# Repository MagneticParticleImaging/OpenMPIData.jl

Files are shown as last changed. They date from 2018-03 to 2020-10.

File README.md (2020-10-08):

# OpenMPIData



The aim of this project is to provide MPI data that are openly available for the research
community and can be freely used. You can find detailed description on the project under
the following link:



## How to give credit
If you use this package please acknowledge us by citing:

T. Knopp, P. Szwargulski, F. Griese, M. Gräser (2020). OpenMPIData: An initiative for freely accessible magnetic particle imaging data. *Data in Brief.* **28** 104971.

A BibTeX file is directly contained within this package `OpenMPIData.bib`.

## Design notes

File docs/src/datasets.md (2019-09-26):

# Datasets

The phantoms have been acquired with specific measurement sequences, MPI scanners, and tracer material.
In the following table an overview about all datasets is given:

## Phantom Measurements

| Study | Experiment Number | Scanner | Sequence | Tracer |
|---|---|---|---|---|
| shapePhantom | 1 | Bruker | 1D Cartesian | Perimag |
| shapePhantom | 2 | Bruker | 2D Lissajous | Perimag |
| shapePhantom | 3 | Bruker | 3D Lissajous | Perimag |
| resolutionPhantom | 1 | Bruker | 1D Cartesian | Perimag |
| resolutionPhantom | 2 | Bruker | 2D Lissajous | Perimag |
| resolutionPhantom | 3 | Bruker | 3D Lissajous | Perimag |
| concentrationPhantom | 1 | Bruker | 1D Cartesian | Perimag |
| concentrationPhantom | 2 | Bruker | 2D Lissajous | Perimag |
| concentrationPhantom | 3 | Bruker | 3D Lissajous | Perimag |
| rotationPhantom | 1 | Bruker | 3D Lissajous | Perimag |
| rotationPhantom | 2 | Bruker | 3D Lissajous | Perimag |
| rotationPhantom | 3 | Bruker | 3D Lissajous | Perimag |

In addition several calibration measurements are available:

## Calibration Measurements

| Study | Experiment Number | Scanner | Sequence | Tracer | Grid | FoV |
|---|---|---|---|---|---|---|
| calibration | 1 | Bruker | 1D Cartesian | Perimag |19x19x19|38x38x19|
| calibration | 2 | Bruker | 2D Lissajous | Perimag |19x19x19|38x38x19|
| calibration | 3 | Bruker | 3D Lissajous | Perimag |19x19x19|38x38x19|
| calibration | 4 | Bruker | 1D Cartesian | Perimag |37x37x37|37x37x18.5|
| calibration | 5 | Bruker | 2D Lissajous | Perimag |37x37x37|37x37x18.5|
| calibration | 6 | Bruker | 3D Lissajous | Perimag |37x37x37|37x37x18.5|
| calibration | 7 | Bruker | 3D Lissajous | Synomag-D |37x37x37|37x37x18.5|
| calibration | 8 | Bruker | 3D Lissajous | Perimag |33x33x27|66x66x27|
| calibration | 9 | Bruker | 3D Lissajous | Perimag |33x33x27|66x66x27|
| calibration | 10 | Bruker | 3D Lissajous | Perimag |33x33x27|66x66x27|
| calibration | 11 | Bruker | 3D Lissajous | Perimag |33x33x27|66x66x27|
| calibration | 12 | Bruker | 3D Lissajous | Perimag |33x33x27|66x66x27|
| calibration | 13 | Bruker | 3D Lissajous | Perimag |33x33x27|66x66x27|
| calibration | 14 | Bruker | 3D Lissajous | Perimag |33x33x27|66x66x27|
| calibration | 15 | Bruker | 3D Lissajous | Perimag |33x33x27|66x66x27|

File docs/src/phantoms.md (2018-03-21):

# Phantoms

Here, we describe the phantoms being used during the MPI measurements. The phantoms are all printed with the stereolithography 3D printing technique. All phantoms share the same robot mount defining the coordinate system. The robot mount is fixed in positive X direction. The flat side marks the positive Z direction. Poistive Y direction is then defined by right hand rule.

You can download the phantoms construction files in the format .SLDPRT, .STL and .STEP.

## Shape Phantom

To resemble a well known shape a cone defined by a **1 mm** radius tip and an apex angle of **10 deg** and a hight of **22 mm**. The total volume is **683.9 µL**. As tracer **Perimag** in a concentration of **50 mmol/L** were used. The phantom can be rendered in 3D resemling the cone or can be cut in a layer view to see either a circle (YZ plane) or a triangle with flattened tip (XZ or XY plane)

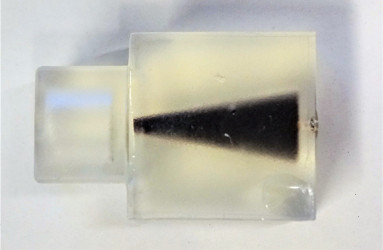
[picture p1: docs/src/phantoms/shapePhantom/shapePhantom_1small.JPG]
ShapePhantom


### CAD Data Shape Phantom

[SolidWorks Part File](./phantoms/shapePhantom/Phantom3_Shape.SLDPRT)
[STL File](./phantoms/shapePhantom/Phantom3_Shape.STL)
[STEP File](./phantoms/shapePhantom/Phantom3_Shape.STEP)

## Resolution Phantom

The resolution phantom consits of 5 tubes filled with **Perimag** featuring a concentration of **50 mmol**.
The 5 tubes have a common origin on one side of the phantom. From there the extend in different angles from this origin within the XY and the YZ plane. As the imaging system features the strong gradient in Z direction the angles in the YZ plane are chosen smaller (**10 deg and 15 deg**) than in XY direction (**20 deg and 30 deg**).
By chosing different planes, one can determine the capable resolution due to different distances of the tubes.

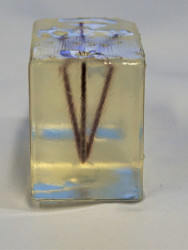
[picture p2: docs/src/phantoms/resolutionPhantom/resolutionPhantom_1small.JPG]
Resolution Phantom


### CAD Data Resolution Phantom

[SolidWorks Part File](./phantoms/resolutionPhantom/Phantom1_Resolution.SLDPRT)
[STL File](./phantoms/resolutionPhantom/Phantom1_Resolution.STL)
[STEP File](./phantoms/resolutionPhantom/Phantom1_Resolution.STEP)

## Concentration Phantom

The second phantom consists of 8 cubes of 2mm edge length resulting in **8µl volume** each. The distance of the cubes are **12 mm** between centers (10 mm between edges)  within the XY plane and 6 between centers (4 mm between corners) within Z direction.
We name the sample chambers 1 to 8 starting with the top layer on the front left (positive X and Y direction), counting clockwise. Then starting with the lower layer with number 5 on the front left (positive X and Y direction), counting clockwise. The concentrations in the 8 sample chambers are diluted with a factor of 1.5 in each step and the values are given in the following table:

|Concentrations| Dilution factor |
| ------ |-------|
| 100 mmol/l  | 0 |
| 66.6 mmol/l | 1.5 |
| 44.4 mmol/l | 2.25 |
| 29.6 mmol/l |3.375 |
| 19.7 mmol/l |5.0625 |
| 13.1 mmol/l |7.59375 |
| 8.77 mmol/l |11.390625 |
| 5.85 mmol/l |17.0859375 |

In the table below the concentrations have been assigned to the indices in the CAD sketch to specify which concentration is placed in which chamber.

|Index in CAD Sketch| Concentrations |
| ------ |-------|
|1| 44.4 mmol/l  |
|2| 100 mmol/l  |
|3| 29.6 mmol/l |
|4| 8.77 mmol/l |
|5| 19.7 mmol/l |
|6| 66.6 mmol/l |
|7| 13.1 mmol/l |
|8| 5.85 mmol/l |

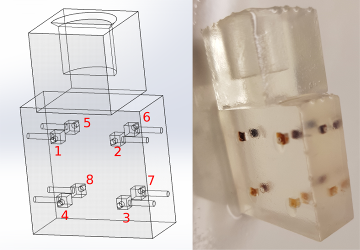
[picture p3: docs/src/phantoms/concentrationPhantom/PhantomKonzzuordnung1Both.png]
ConcentrationPhantom


### CAD Data Concentration Phantom

[SolidWorks Part File](./phantoms/concentrationPhantom/Phantom2_Concentration.SLDPRT)
[STL File](./phantoms/concentrationPhantom/Phantom2_Concentration.STL)
[STEP File](./phantoms/concentrationPhantom/Phantom2_Concentration.STEP)

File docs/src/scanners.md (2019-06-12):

# MPI Scanners

Here we describe the MPI scanners being used to acquire the MPI data

## Bruker Preclinical MPI Scanner

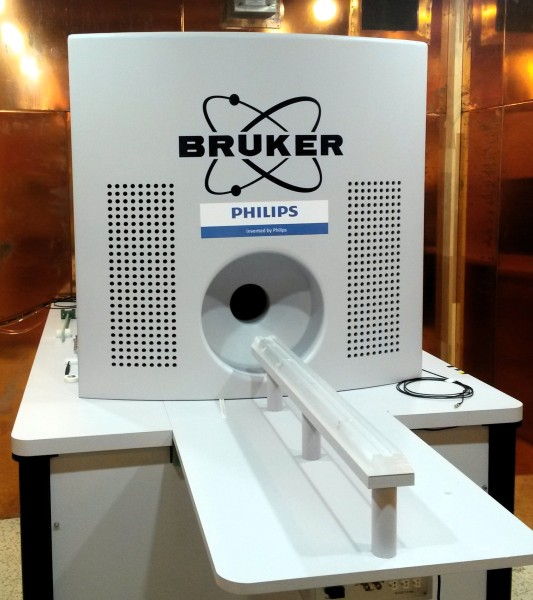
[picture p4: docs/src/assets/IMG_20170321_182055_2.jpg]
Bruker Preclinical MPI Scanner


The preclinical MPI scanner from Bruker has a 118 mm bore and is equipped
with a fully 3D send/receive system and 3D focus fields allowing for
flexible measurement sequencies. The system parameters are given below

| Parameter                     |     Value                           |
| ------------------------------| ------------------------------------|
| Scanner Bore Diameter         |   118 mm                            |
| MaxDrive-Field Amplitude      |   14 mT x 14 mT x 14 mT             |
| MaxFocus-Field Amplitude      |   17 mT x 17 mT x 42 mT             |
| Drive-Field Frequency         |   2.5MHz/102 x 2.5MHz/96 x 2.5MHz/99|
| Max Selection-Field Gradient  |   -1.25 T/m x -1.25 T/m x 2.5 T/m   |
| Repetition Time               |    38.4 $\mu$s - 21.54 ms           |

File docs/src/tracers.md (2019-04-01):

# Tracers

As MPI is a tracer based imaging modality, it is important to relate all
measurements to the tracer being used. Currently most datasets are measured with perimag and
one system matrix is measured with synomag-D.

## Perimag
[Perimag](https://www.micromod.de/de/produkte-197-magnetisch_peri.html) is a dextran coated tracer from the
company Micromod. Perimag offers a very good MPI signal comparable to Resovist and can be directly ordered, which is essential for reproducible research.

## Synomag-D
[Synomag-D](https://www.micromod.de/en/produkte-230-magnetic_syno.html) is a dextran coated tracer from the
company Micromod as well. It provides up to a factor of 2 better signal than perimag.

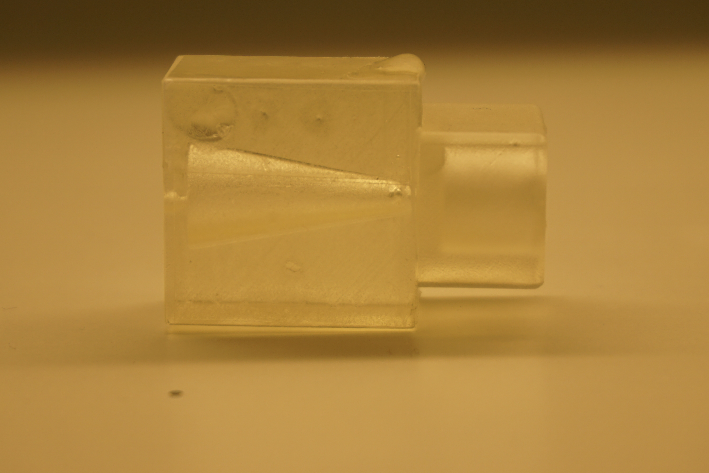
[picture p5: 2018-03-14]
docs/src/phantoms/shapePhantom/shapePhantom1.JPG

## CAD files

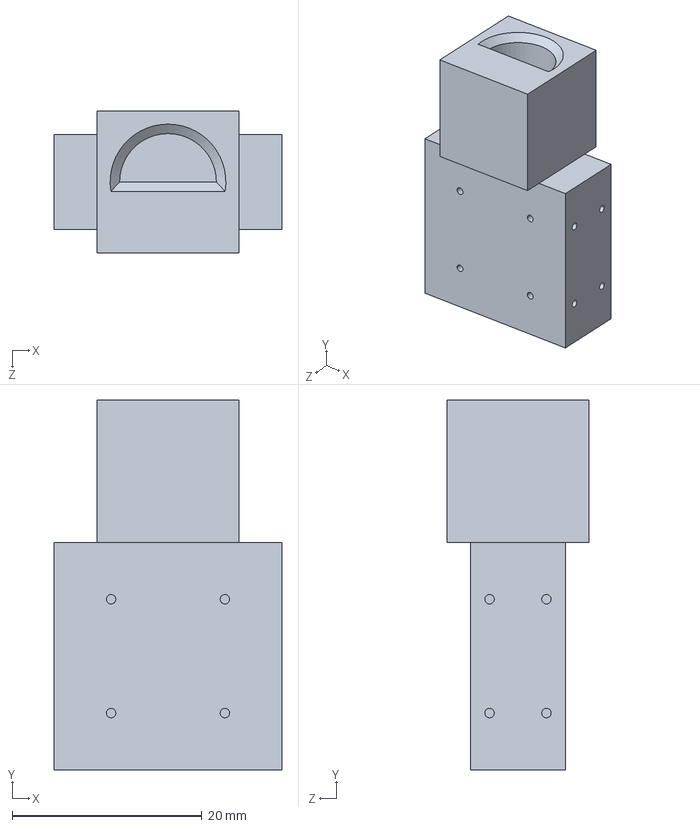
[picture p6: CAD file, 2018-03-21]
docs/src/phantoms/concentrationPhantom/Phantom2_Concentration.STEP
24.0 x 39.0 x 15.0 mm

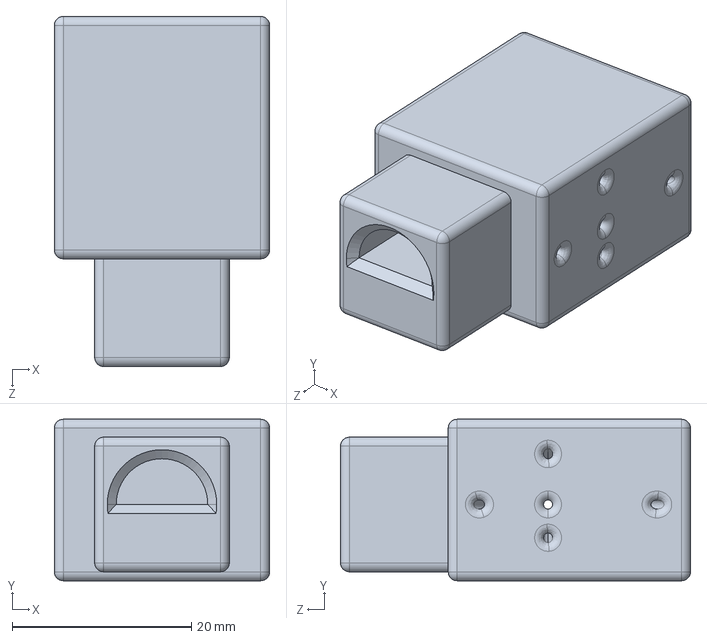
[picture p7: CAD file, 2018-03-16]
docs/src/phantoms/resolutionPhantom/Phantom1_Resolution.STEP
24.0 x 18.0 x 39.0 mm

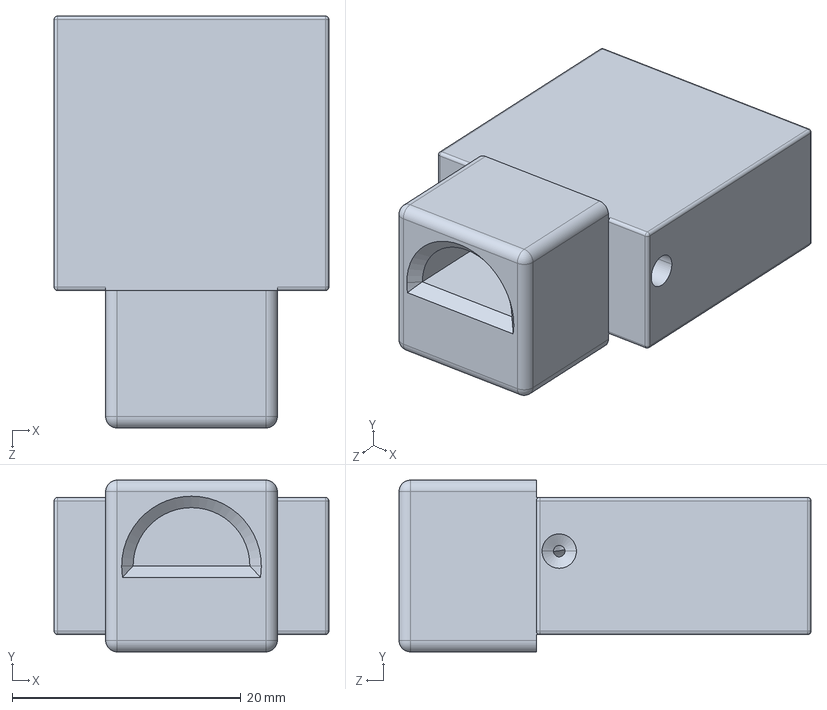
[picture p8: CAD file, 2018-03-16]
docs/src/phantoms/shapePhantom/Phantom3_Shape.STEP
24.0 x 15.0 x 36.0 mm

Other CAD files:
docs/src/phantoms/concentrationPhantom/Phantom2_Concentration.SLDDRW
docs/src/phantoms/concentrationPhantom/Phantom2_Concentration.SLDPRT
docs/src/phantoms/concentrationPhantom/Phantom2_Concentration.STL
docs/src/phantoms/resolutionPhantom/Phantom1_Resolution.SLDDRW
docs/src/phantoms/resolutionPhantom/Phantom1_Resolution.SLDPRT
docs/src/phantoms/resolutionPhantom/Phantom1_Resolution.STL
docs/src/phantoms/shapePhantom/Phantom3_Shape.SLDPRT
docs/src/phantoms/shapePhantom/Phantom3_Shape.STL
docs/src/phantoms/shapePhantom/Phantom3_shape.SLDDRW

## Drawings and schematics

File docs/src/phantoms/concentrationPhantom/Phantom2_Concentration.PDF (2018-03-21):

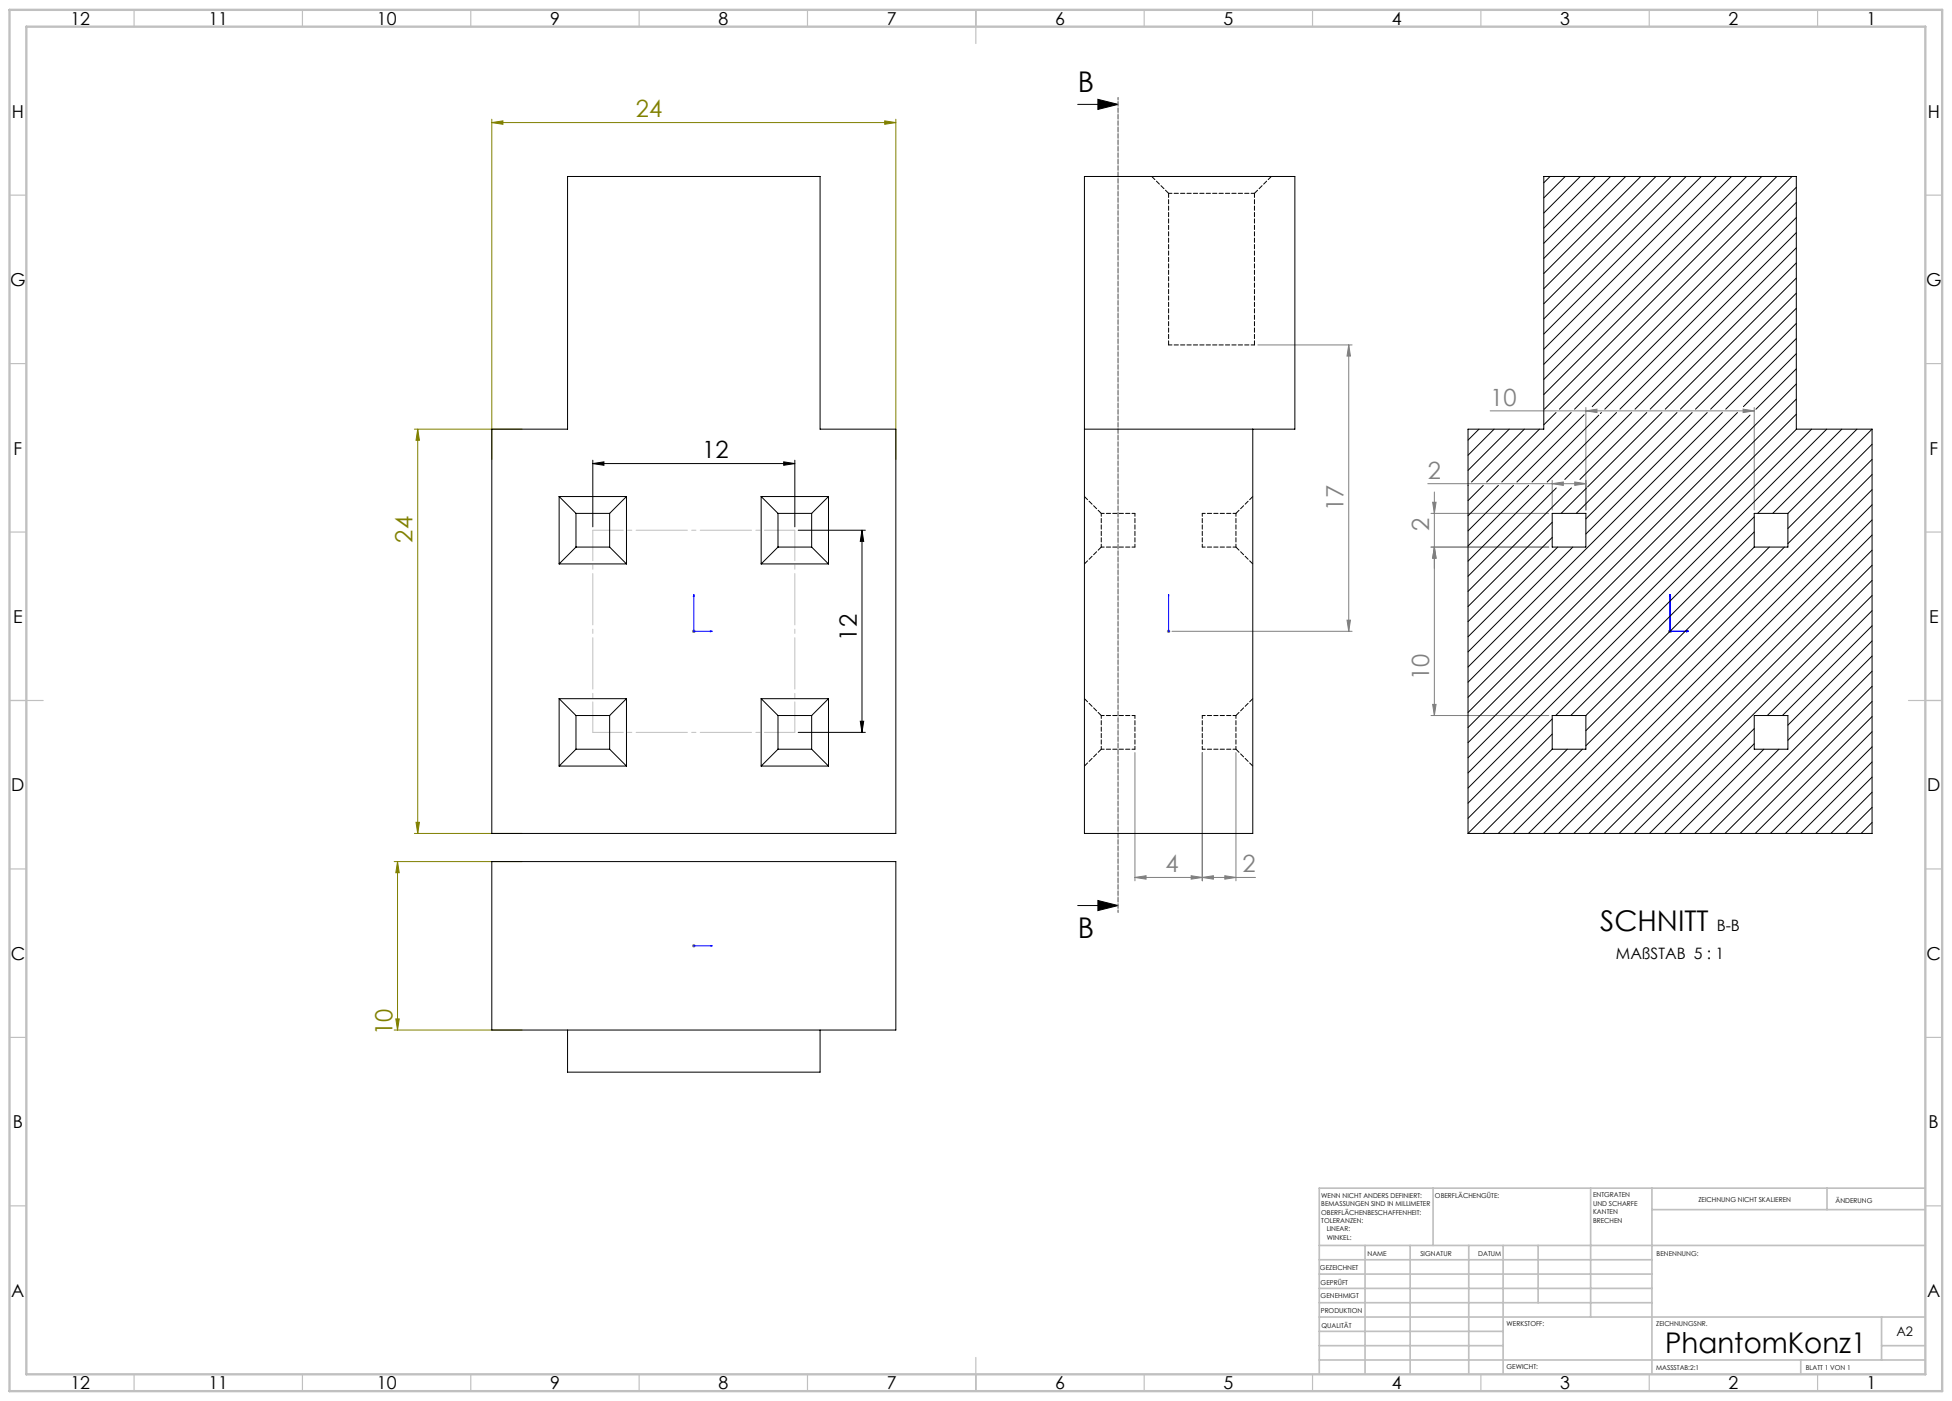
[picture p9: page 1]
SCHNITT B-B; MAßSTAB 5 : 1; MASSSTAB:2:1; BLATT 1 VON 1; ZEICHNUNG NICHT SKALIEREN; ÄNDERUNG; UND SCHARFE; WENN NICHT ANDERS DEFINIERT:; OBERFLÄCHENGÜTE:

BEMASSUNGEN SIND IN MILLIMETER
OBERFLÄCHENBESCHAFFENHEIT:
TOLERANZEN:
LINEAR:
WINKEL:

NAME | SIGNATUR | DATUM | | | | BENENNUNG:
QUALITÄT | | | | WERKSTOFF: | ZEICHNUNGSNR. PhantomKonz1 GEWICHT: | A2

GEZEICHNET
GEPRÜFT
GENEHMIGT
PRODUKTION

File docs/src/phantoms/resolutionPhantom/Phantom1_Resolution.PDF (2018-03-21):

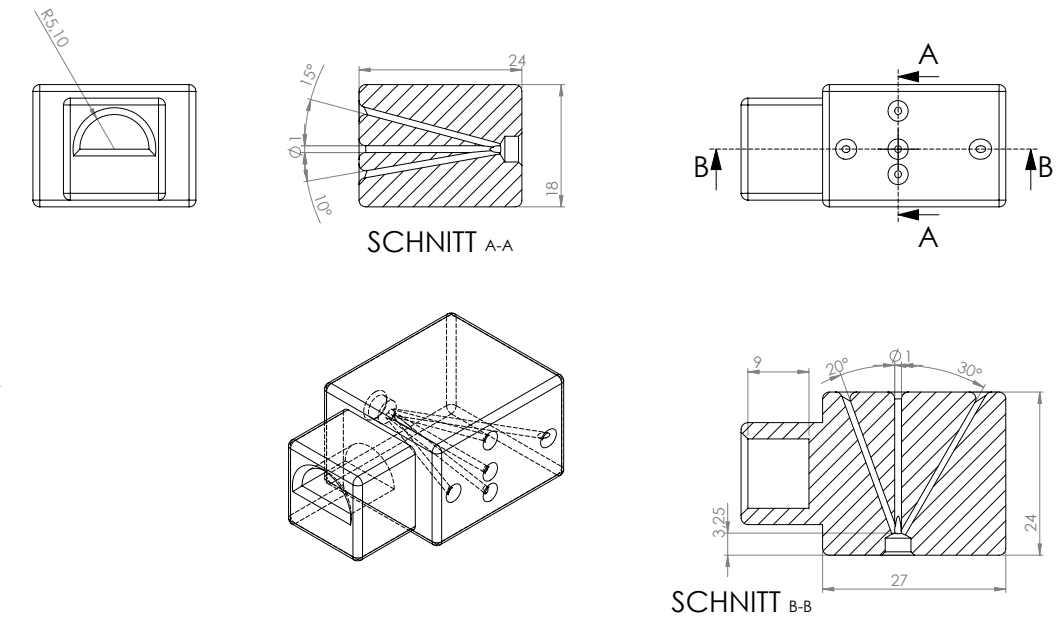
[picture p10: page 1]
SCHNITT A-A; SCHNITT B-B

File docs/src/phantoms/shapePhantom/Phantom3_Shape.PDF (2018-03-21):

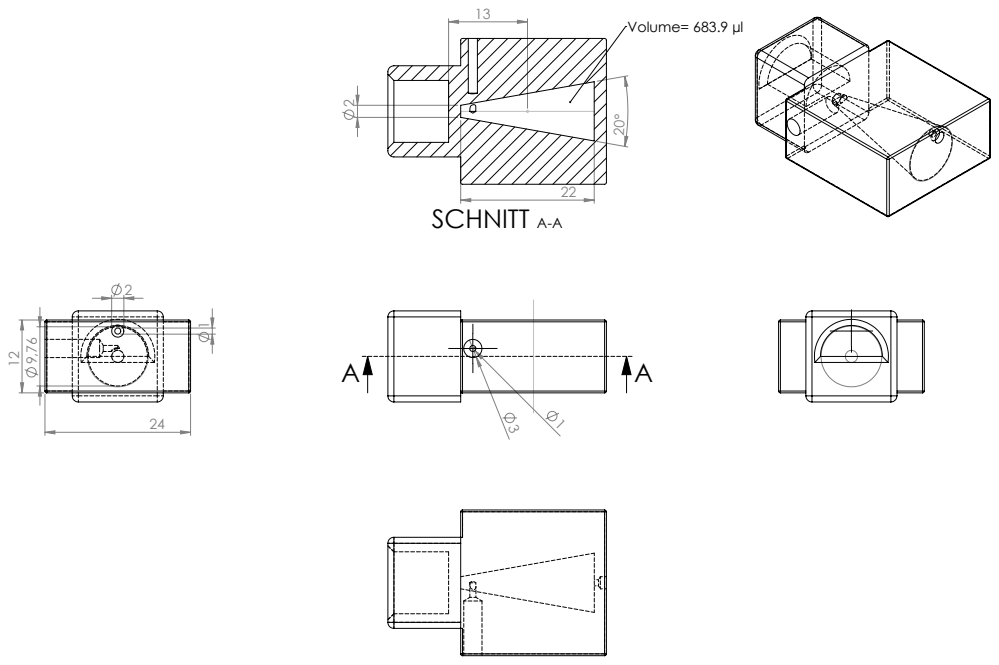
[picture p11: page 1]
SCHNITT A-A; Volume= 683.9 µl

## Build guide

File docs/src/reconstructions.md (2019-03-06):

### Reconstructions

Reconstruction results for the different phantoms and measurements sequences are shown below.

## Shape Phantom Reconstructions
### 1D Reconstruction
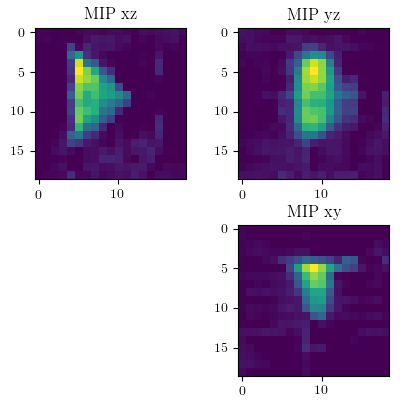
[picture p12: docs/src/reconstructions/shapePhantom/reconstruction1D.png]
ShapePhantom

### 2D Reconstruction
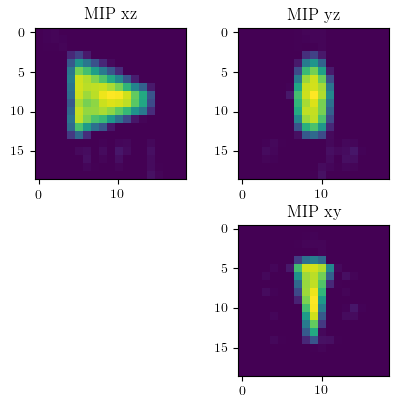
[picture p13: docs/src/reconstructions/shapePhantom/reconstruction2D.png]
ShapePhantom

### 3D Reconstruction
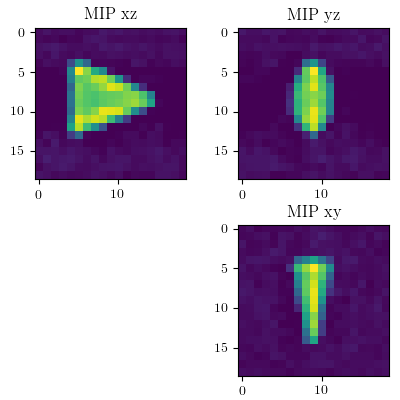
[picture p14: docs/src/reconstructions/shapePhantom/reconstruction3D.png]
ShapePhantom


## Reolution Phantom Reconstruction
### 1D Reconstruction
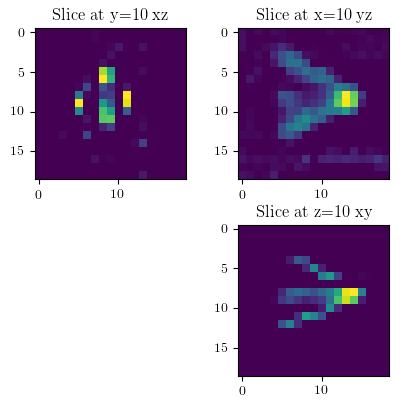
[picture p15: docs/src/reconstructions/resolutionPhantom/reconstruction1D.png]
ResolutionPhantom

### 2D Reconstruction
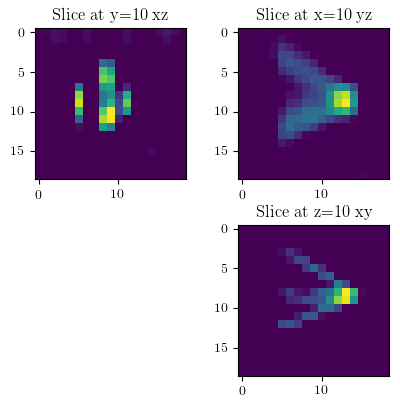
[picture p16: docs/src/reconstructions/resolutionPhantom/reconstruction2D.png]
ResolutionPhantom

### 3D Reconstruction
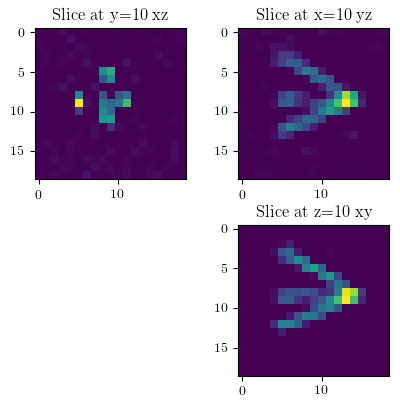
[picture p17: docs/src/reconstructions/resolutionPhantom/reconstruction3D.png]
ResolutionPhantom


## Concentration Phantom Reconstruction
### 1D Reconstruction Slice 7,7,7
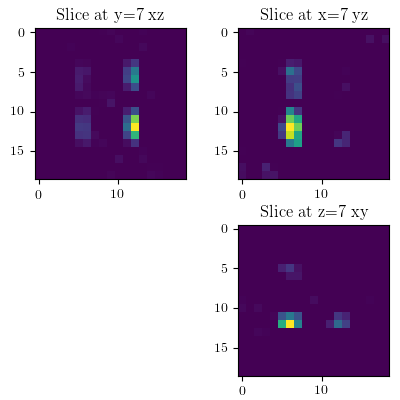
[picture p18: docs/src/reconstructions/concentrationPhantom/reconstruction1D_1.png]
ConcentrationPhantom

### 1D Reconstruction Slice 13,13,13
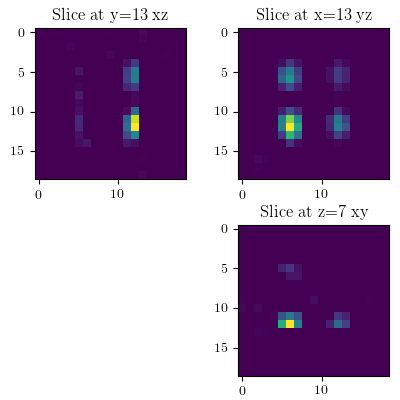
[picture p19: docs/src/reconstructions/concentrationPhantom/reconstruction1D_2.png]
ConcentrationPhantom

### 2D Reconstruction Slice 7,7,7
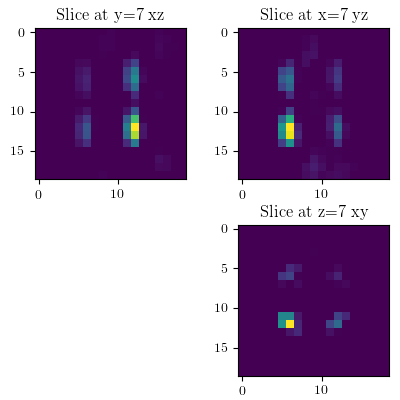
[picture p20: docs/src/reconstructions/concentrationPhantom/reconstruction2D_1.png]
ConcentrationPhantom

### 2D Reconstruction Slice 13,13,13
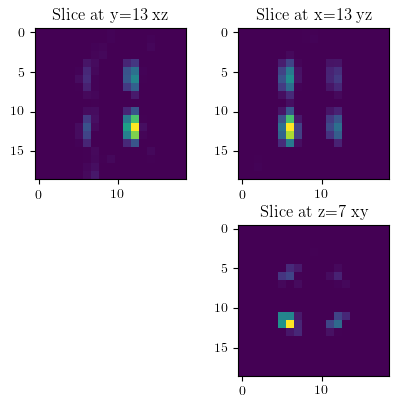
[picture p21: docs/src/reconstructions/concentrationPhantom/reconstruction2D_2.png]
ConcentrationPhantom

### 3D Reconstruction Slice 7,7,7
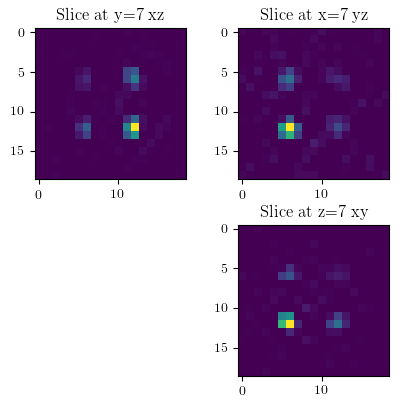
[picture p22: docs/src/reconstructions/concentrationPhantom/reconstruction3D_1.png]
ConcentrationPhantom

### 3D Reconstruction Slice 13,13,13
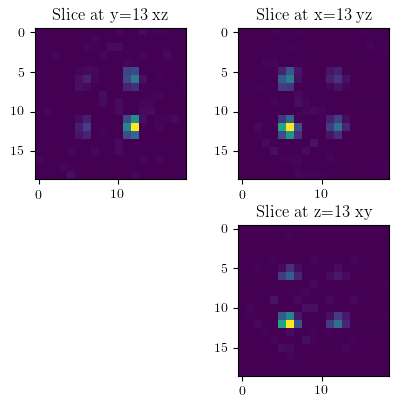
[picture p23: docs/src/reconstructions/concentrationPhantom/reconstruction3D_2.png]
ConcentrationPhantom


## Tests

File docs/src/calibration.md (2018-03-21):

# Calibration

When using a system matrix based reconstruction algorithm one
usually uses calibration data to setup the system matrix. In the
following we describe measured calibration datasets.

Each calibration dataset is acquired with a small sample of
a specific tracer representing an image voxel. The delta sample
is placed at various positions within the target FOV and calibration
measurements are taken.

Even for 1D and 2D sequences we measured the system matrix on a 3D grid.
While this is not strictly necessary for image reconstruction it can be
very usefull when studying the particle physics. It is advised to extract
appropriate slices prior to reconstruction.

All calibration datasets are also acquired outside the drive-field FOV.
This "overscanning" is essential to avoid particles from outside the
FOV influencing the reconstruction result inside the FOV. The overscan
may be manually shrinked prior to reconstruction

Tracer [Perimag](https://www.micromod.de/de/produkte-197-magnetisch_peri.html) (100 mmol), Delta Sample 2mm x 2mm x 1mm
Before each measurment a 30 minute Warm Up has been applied
# 1D Sequence

| Parameter                  |     Value                                |
| ---------------------------| ---------------------------------------- |
| Drive-Field Amplitude      |   12 mT x 0mT x 0 mT                     |
| Drive-Field Frequency      |   2.5 MHz/102 x 2.5 Mhz/96 x 2.5 Mhz/99  |
| Selection-Field Gradient   |   -1.0 T/m x -1.0 T/m x 2.0 T/m          |
| Sampled Field of View      |   24 mm x 24 mm x 12 mm                  |
| Grid size                   |   19  x 19  x 19                        |
| Repetition Time            |    40.8 $\mu$s                           |
| Number of Averages         |    1000                                  |
| Number of Background Scans |    362                                  |

# 2D Lissajous Sequence

| Parameter                  |     Value                                |
| ---------------------------| ---------------------------------------- |
| Drive-Field Amplitude      |   12 mT x 12 mT x 0 mT                   |
| Drive-Field Frequency      |   2.5 MHz/102 x 2.5 Mhz/96 x 2.5 Mhz/99  |
| Selection-Field Gradient   |   -1.0 T/m x -1.0 T/m x 2.0 T/m          |
| Sampled Field of View      |   24 mm x 24 mm x 12 mm                  |
| Grid size                   |   19  x 19  x 19                         |
| Repetition Time            |    652.8 $\mu$s                          |
| Number of Averages         |    1000                                  |
| Number of Background Scans |    362                                  |

# 3D Lissajous Sequence
| Parameter                  |     Value                                |
| ---------------------------| ---------------------------------------- |
| Drive-Field Amplitude      |   12 mT x 12 mT x 12 mT                  |
| Drive-Field Frequency      |   2.5 MHz/102 x 2.5 Mhz/96 x 2.5 Mhz/99  |
| Selection-Field Gradient   |   -1.0 T/m x -1.0 T/m x 2.0 T/m          |
| Sampled Field of View      |   24 mm x 24 mm x 12 mm                  |
| Grid size                   |   19  x 19  x 19                         |
| Repetition Time            |    21.54 ms                              |
| Number of Averages         |    1000                                  |
| Number of Background Scans |    362                                  |

## Transfer Function

Currently the transfer function of the receive chain is not included in the measured data.
However, we plan to include them in the datasets soon.

<!--  All datasets include the transfer function of the receive chain. One has
to divide the measured frequency data by this transfer function in order
to get corrected signals. This is in particular important when interpreting
time signals. -->

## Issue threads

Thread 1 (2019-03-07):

### ISSUE TITLE
Unit of Scanner Bore Diameter

### ISSUE THREAD

**Issue by jhnnslschnr** [MagneticParticleImaging/OpenMPIData.jl#1]
The scanner bore diameter is stated to be 11.8 mm in the table [here](https://magneticparticleimaging.github.io/OpenMPIData.jl/latest/scanners.html), while i guess it should be 11.8 cm (like in the text above).

**Comment by tknopp** [comment]
thanks. Should be fixed by https://github.com/MagneticParticleImaging/OpenMPIData.jl/commit/f88279bfbc234ed32ede31bbcfd623f8a363fdb2

Will close once the documentation is build.

**Comment by jbeuke** [comment]
The same error is also in the text above the table.

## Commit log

2017-05-09 add parameter in calibration, scanners and sequences
2018-03-15 add missing bracket
2018-03-15 Added CAD and STL Files for Phantom 2
    [Phantom2_Concentration.SLDPRT, Phantom2_Concentration.STEP, Phantom2_Concentration.STL, Phantom2_Cover.SLDPRT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]
2018-03-15 Added STL and CAD Files for Phantom 1
    [Phantom1_Resolution.SLDPRT, Phantom1_Resolution.STEP, Phantom1_Resolution.STL]
2018-03-15 Added CAD and STL files for Phantom 3
    [Phantom3_Shape.SLDPRT, Phantom3_Shape.STEP, Phantom3_Shape.STL]
2018-03-15 Added CAD Drawings
    [Phantom1_Resolution.SLDDRW, Phantom2_Concentration.SLDDRW, Phantom3_shape.SLDDRW]
2018-03-20 Inserted missing data. Added CAD links
2018-03-20 Update CAD files for concentration phantom
    [Phantom2_Concentration.SLDPRT, Phantom2_Concentration.STEP, Phantom2_Concentration.STL, Phantom2_Cover.SLDPRT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]
